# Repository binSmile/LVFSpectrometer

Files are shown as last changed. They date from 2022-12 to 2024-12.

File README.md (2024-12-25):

# LVFSpectrometer
[
](https://www.youtube.com/watch?v=VhedL_mU17M)

 Spectrometer based on linear variable filter with pulse-counter

The main idea was born, from need on spectral measurements of really weak light source (Scanning Tunneling Microscopy Light Emission).

My system consist of several parts:
- IDQuantique ID120 Single photo counter, Avalanced Photo Diode (APD) (with LV-TTL output)
- Optical system based on Thorlab's Cage system with several mirrors, beam splitter (90:10) and laser diode for illumination of collection point
- ESP8266 used as TTL pulse counter from APD (also used as DAC) 
- Linear Variable Filter (LVF) by Ocean Optics (now Ocean Insight) for 300-750 nm range.
- Arduino UNO used for movement step motor control
- Step driver TB6600
- 3D printed LVF holder.

Let's describe each part.
## DAC and pulse counter
In folder **Controllers**, you found ESPPulseCounter.ino - firmware for ESP8266. 
Previously it works on Arduino too, but it has some lags and minimal pulses integration time was 20 ms. ESP8266 - works better, the best time is 7 ms.
Before flashing firmware to ESP, you should set integration time, and minimum and maximum counting levels in Hz (counts per second), which correspond to 0V and 5V levels on DAC.

The main problem of counting pulses from is very short pulses from APD. Output pulse width is 25 **ns**. 
For counting, I use M74HC4040 (or SN74HC4040N) 12-Bit Asynchronous Binary Counters. And collect the number by MCP23017, 16-bit input/output port expander.  The ESP reads the number for one clock from port-extender. After that, the number was sent to serial and to MCP4725 12-bit DAC.
The DAC output was connected with Omicron Microscope to Aux2-port.
The layout of interconnection you can see in ESPPulseCounter-connection.svg

### Pulse_grabber.py
At the first time, I used simple python serial port grabber for collection information about intensity. At start of the script, it read a file with ESP firmware and store in file the values of DAC settings (such as min/max counts and integration time). These values may be used by some scripts for analyzing of Omicron Experimental Data.
This program writes counts to txt file and zip it in the end of work.

## Linear Variable Filter
I had a linear Variable Filter by Ocean Optics (You can read more here [Ocean Insight](https://www.oceaninsight.com/products/sampling-accessories/solid-sampling/linear-variable/lvf-hh/?qty=1)). 

## 3D-models
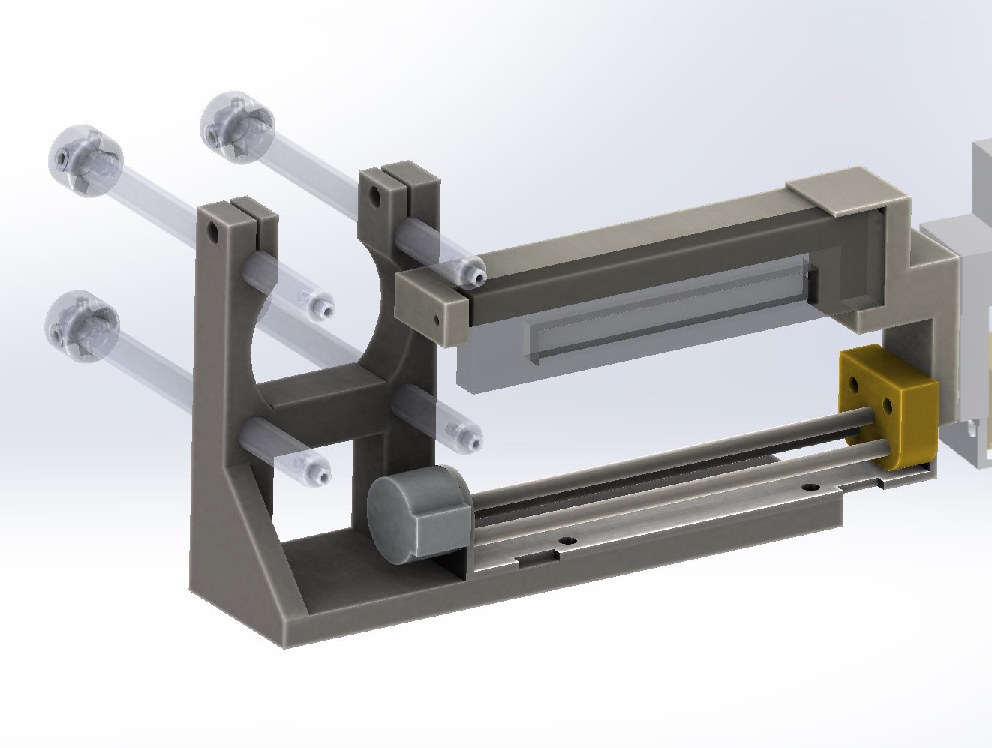
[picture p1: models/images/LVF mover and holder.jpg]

You can find models created in SolidWorks, I share to you the holder of LVF filter, and cage-holder for step-motor actuator.
If you plan to use it,  I recommend to you: paint model to black color,  and modify it for decreasing of shadows on light path. Also, in one of edge position, you will have touch of LVF-holder  with cage.

## Actuator
I bought  an assembled actuator with step motor from Aliexpress . It has DC 4-9 V  power supply. And it has driven by TB6600 step driver. I use 1/800 regime on driver, and it means, that driven shaft will have 12800 steps for 90 mm rod. 

## Arduino Move controller
You can find MoveControl.ino with Arduino Uno firmware and MoveControl-connection with connection layout. Also, I applied [GyverStepper2](https://alexgyver.ru/gyverstepper/). This is an excellent lib for stepper control.
For controlling of Arduino by serial, I used a simple communication  language presented is SerialCommunication-example sketch.

### Wires
- D4 to ENA+
- D3 to DIR+
- D2 to PUL+

### Commands for move controlling
Comand's structure is:
"Device","Comand","Value"
In this case the device number is **002**

- **002,brake,0** - stop
- **002,move,777** move on 777 steps forward
- **002,setspeed,-666** backward movement with speed 666 steps per piece of time
- **002,reset,0** set zero position 0

#### Service commands:
- **002,ready,0** return **m** - move, **r** - ready
- **002,Current,0** curent position
- **002,getStatus,0** 
- **002,setaccel,333** - you can set acceleration in step per sec^2. Set Zero is means movement with maximal speed, without smooth acceleration.

## SpecAcquisition.py
This is main programm for spectra Acusition.
Usually, I start it from console and use comand interface for experiment proceeding.
Todo: check stable work with long acqusition, more then 10 minutes.

### Main functions
- **GoHome()** - Function for manual approaching to home position. Setup doesn't have end move buttons.
- **DoPointSpectra(points=20,exposition=2,LVFLen=12000,name=SpecName)** - this command do 20 stops during 12000 steps lenght of movement, with 2 second acuqsition on each stop.

## SpecReader.py
Simple plotter of measured spectra.

## File tree
```
.
├── controllers                           - firmwares
│   ├── ESPPulseCounter-connection.svg    - wire connection DAC
│   ├── ESPPulseCounter.ino - ESP arduino - like firmware for pulse-counter DAC
│   ├── MoveControl-connection.svg        - wire connection of LVF mover
│   ├── MoveControl.ino                   - firmware for LVF mover
│   └── SerialCommunication-example.ino   - example of simple commmunication between PC and arduino.
├── models                                - directory with 3d-models for printing of LVF-holder.
│   ├── IDQ-LD.SLDASM
│   └── ...
├── README.md
├── Pulse_grabber.py                      - Loging of pulses from counter
├── SpecAcquisition.py                    - programm for Spectum acqusition with LFV
└── SpecReader.py                         - Simple plotter
```

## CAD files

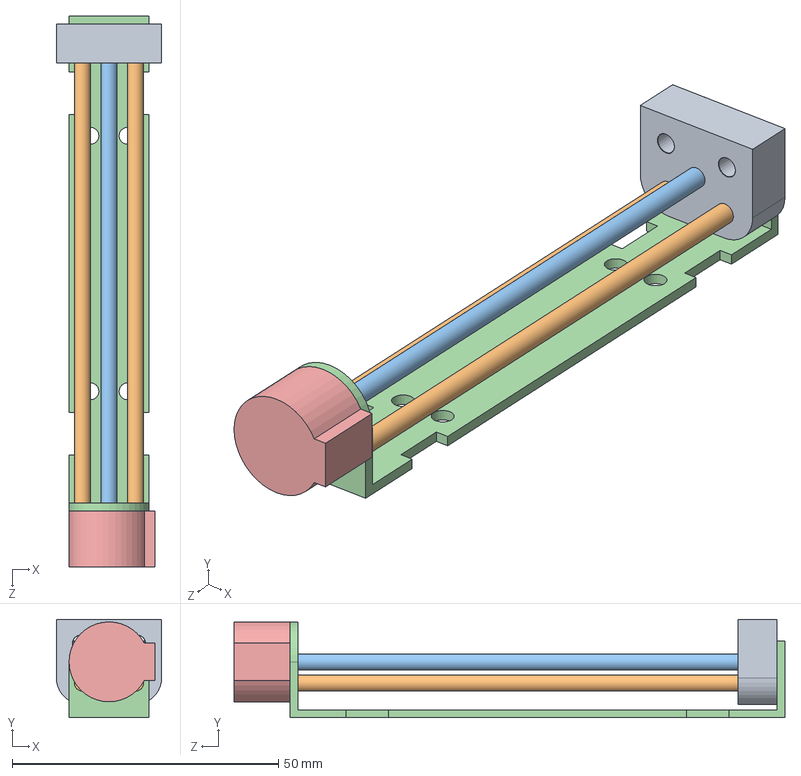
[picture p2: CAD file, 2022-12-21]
models/LinearMover.SLDASM
19.8 x 18.5 x 103.5 mm
Каретка^LinearMover
Направляющие^LinearMover
Ось^LinearMover
Станина^LinearMover
Мотор^LinearMover

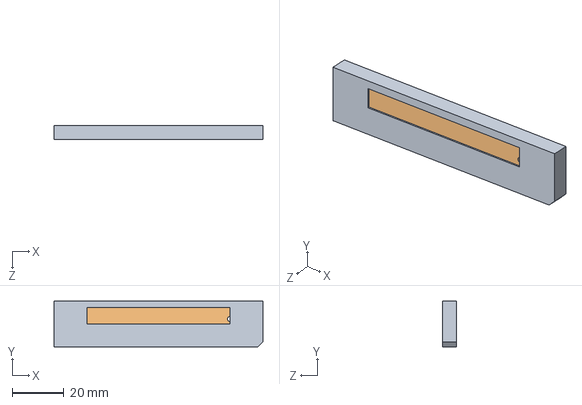
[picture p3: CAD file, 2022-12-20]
models/LVF.SLDASM
81.1 x 17.8 x 5.34 mm
LVF body
LVF glass

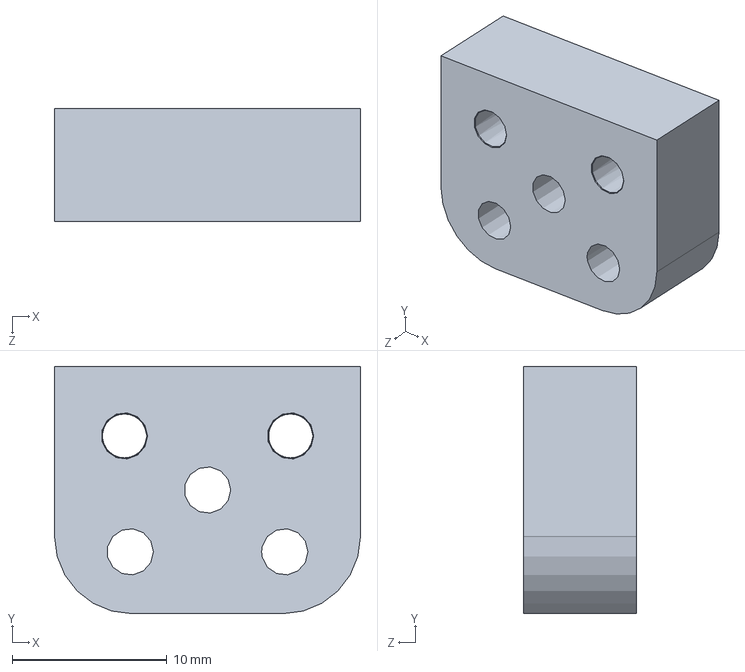
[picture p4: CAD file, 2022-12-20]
models/Каретка^LinearMover.SLDPRT
19.8 x 16.0 x 7.30 mm

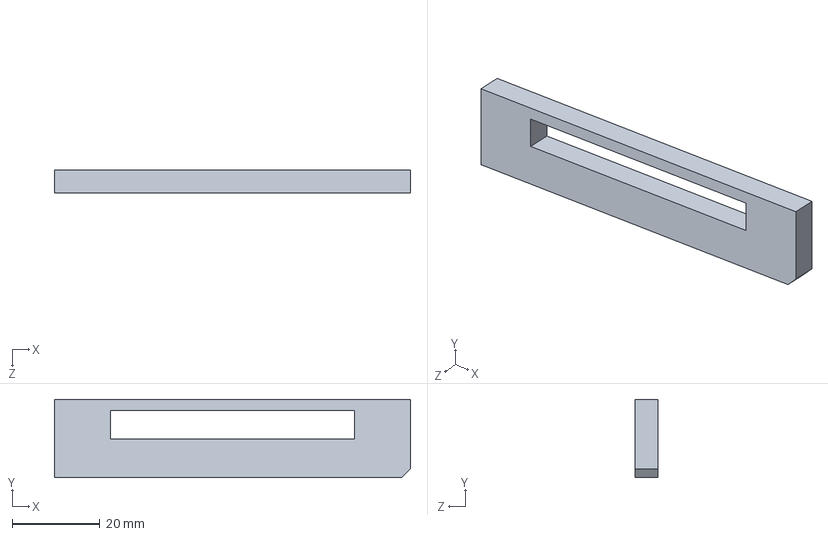
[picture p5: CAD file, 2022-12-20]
models/LVF body.SLDPRT
81.1 x 17.8 x 5.34 mm

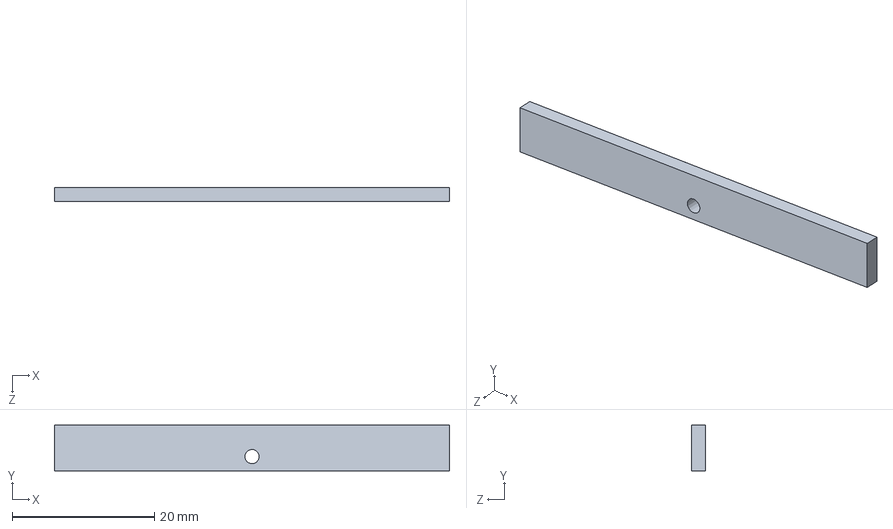
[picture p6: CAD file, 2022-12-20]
models/LVF glass.SLDPRT
55.5 x 6.41 x 2.00 mm

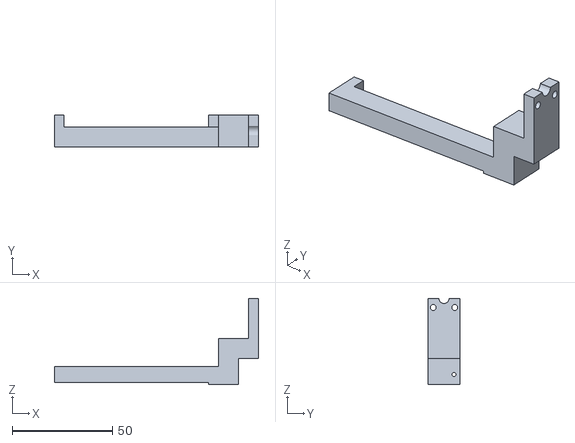
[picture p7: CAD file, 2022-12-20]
models/Скоба2^LVF holder_IDQ-LD.STL
102.0 x 16.0 x 43.0

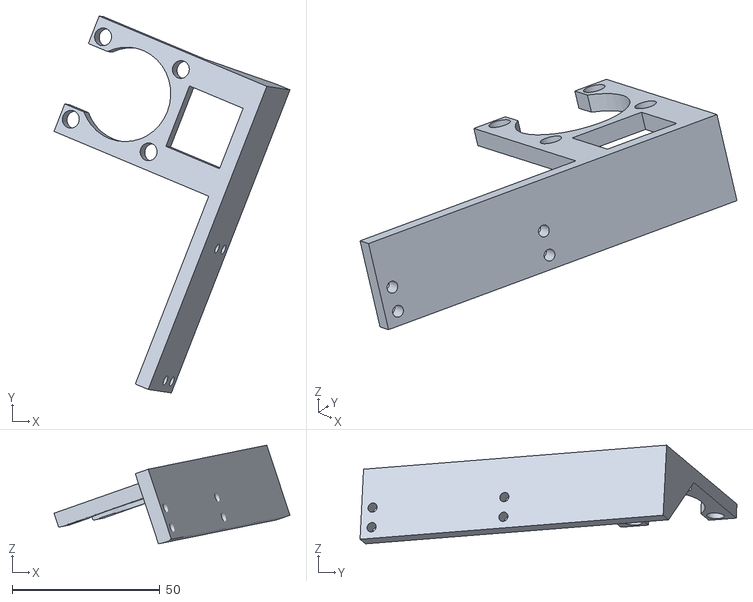
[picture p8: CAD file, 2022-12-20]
models/StepDriver holder^IDQ-LD.STL
79.8 x 127.5 x 33.4

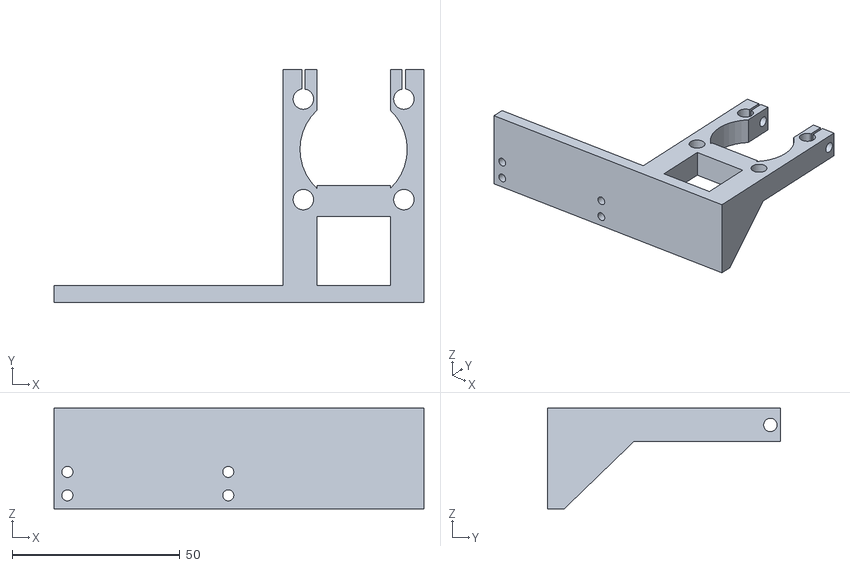
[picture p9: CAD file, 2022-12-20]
models/Деталь1^StepDriver holder_IDQ-LD.STL
110.4 x 69.5 x 30.0

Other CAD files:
models/OceanOptics-корпус.SLDPRT

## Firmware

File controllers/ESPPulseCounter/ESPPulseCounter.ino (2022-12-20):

int mestime = 10; // ms
long maxValue = 10800; // Hz
int noise = 800; // Hz

#include <Adafruit_MCP23X17.h>
#define BCMR D5
#define BCQ1 0
#define BCQ2 1
#define BCQ3 2
#define BCQ4 3
#define BCQ5 4
#define BCQ6 5
#define BCQ7 6
#define BCQ8 7
#define BCQ9 8
#define BCQ10 9
#define BCQ11 10
#define BCQ12 11

#define BCQ13 12
#define BCQ14 13
#define BCQ15 14
#define BCQ16 15
float outValue = 0;

Adafruit_MCP23X17 mcp;
#include <Wire.h>
#include <Adafruit_MCP4725.h>
Adafruit_MCP4725 dac;

// Set this value to 9, 8, 7, 6 or 5 to adjust the resolution
#define DAC_RESOLUTION    (12)

#include <string.h>
char unitID_in[10];
char command_in[10];
char data_in[100];

void setup() {
  Serial.begin(115200);
    Serial.flush();
  //while (!Serial);
  //  Serial.println("MCP23017  Button Test!");

  // uncomment appropriate mcp.begin
  if (!mcp.begin_I2C()) {
    Serial.println("Error.");
    while (1);
  }
  //  mcp.begin(0x20);

  // configure pin for port extender
  mcp.pinMode(BCQ1, INPUT);
  mcp.pinMode(BCQ2, INPUT);
  mcp.pinMode(BCQ3, INPUT);
  mcp.pinMode(BCQ4, INPUT);
  mcp.pinMode(BCQ5, INPUT);
  mcp.pinMode(BCQ6, INPUT);
  mcp.pinMode(BCQ7, INPUT);
  mcp.pinMode(BCQ8, INPUT);
  mcp.pinMode(BCQ9, INPUT);
  mcp.pinMode(BCQ10, INPUT);
  mcp.pinMode(BCQ11, INPUT);
  mcp.pinMode(BCQ12, INPUT);

  mcp.pinMode(BCQ13, INPUT);
  mcp.pinMode(BCQ14, INPUT);
  mcp.pinMode(BCQ15, INPUT);
  mcp.pinMode(BCQ16, INPUT);
  pinMode(BCMR, OUTPUT);
  dac.begin(0x60);
  digitalWrite(BCMR, LOW);
  digitalWrite(BCMR, HIGH);
  digitalWrite(BCMR, LOW);
  
}

void loop() {
  
static uint32_t tmr2;
if (millis() - tmr2 > mestime) {
  tmr2 = millis();

  //    uint8_t PA = mcp.readGPIO(0);
  uint16_t PAB = mcp.readGPIO();
  unsigned int value = PAB & 0b00001111111111111;
  //    unsigned int value = 0b00001111111111111;
  Serial.println(PAB, DEC);
  digitalWrite(BCMR, HIGH);
  digitalWrite(BCMR, LOW);


  //    int qState[] = {
  //      mcp.digitalRead(BCQ12), mcp.digitalRead(BCQ11), mcp.digitalRead(BCQ10), mcp.digitalRead(BCQ9), mcp.digitalRead(BCQ8), mcp.digitalRead(BCQ7), mcp.digitalRead(BCQ6), mcp.digitalRead(BCQ5), mcp.digitalRead(BCQ4), mcp.digitalRead(BCQ3), mcp.digitalRead(BCQ2), mcp.digitalRead(BCQ1)
  //    };
  //    unsigned int value = 0;
  //    for (byte i = 0; i < 12; i++)
  //    {
  //      value *= 2;
  //      value += qState[i] ;
  //    }
  //    value = value / 2;
  unsigned long freq = value * 1e3 / mestime;
  //Serial.println(value, DEC); // OUTPUT TRUE

  //Serial.println(freq, DEC);
  if (freq < noise) {
    freq = noise;
    outValue = 0;
  }
  else {
    outValue = (freq - noise);
    outValue = (outValue / maxValue) * (4095);
    outValue = int(outValue);
    if (outValue > 4095) {
      outValue = 4095;
    }
  }
  outValue = (freq - noise);
  outValue = (outValue / maxValue) * (4095);
  outValue = int(outValue);
  if (outValue > 4095) {
    outValue = 4095;
  }


  dac.setVoltage(outValue, false);
  //    outValue = 0;
  //    value = 0;

}

}

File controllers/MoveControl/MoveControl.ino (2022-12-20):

const uint8_t pin_ENA = 4;                // Вывод Arduino подключённый к входу драйвера ENA+.
const uint8_t pin_DIR = 3;                // Вывод Arduino подключённый к входу драйвера DIR+.
const uint8_t pin_PUL = 2;                // Вывод Arduino подключённый к входу драйвера PUL+.
// Вывод GND Arduino соединён с входами драйвера ENA-, DIR-, PUL-.
#include <GyverStepper2.h>
//https://alexgyver.ru/gyverstepper/
//GStepper<STEPPER2WIRE> stepper(1, pin_PUL, pin_DIR, pin_ENA);
GStepper2<STEPPER2WIRE> stepper(1, 2, 3, 4);

#include <string.h>
char unitID_in[10];
char command_in[10];
char data_in[100];


void setup() {                            //
  //  pinMode( pin_ENA, OUTPUT );          // Конфигурируем вывод Arduino как выход.
  //  pinMode( pin_DIR, OUTPUT );          // Конфигурируем вывод Arduino как выход.
  //  pinMode( pin_PUL, OUTPUT );          // Конфигурируем вывод Arduino как выход.
  Serial.begin(2000000);
  pinMode(13, OUTPUT); // Sets pin 13 as OUTPUT.
  Serial.flush();

  // установка макс. скорости в шагах/сек
  stepper.setMaxSpeed(400);
  // установка ускорения в шагах/сек/сек
  stepper.setAcceleration(500);

  // отключать мотор при достижении цели
  stepper.autoPower(true);
  // положительные смещения - от мотора
  stepper.reverse(false);


}                                         //
//



void loop() {
  stepper.tick();

    // график положения
    static uint32_t tmr2;
    if (millis() - tmr2 > 20) {
      tmr2 = millis();
      Serial.println(stepper.getCurrent());
    }



  int i = 0;
  char buffer[100];

  //если есть данные - читаем
  if (Serial.available()) {
    delay(100);

    //загоняем прочитанное в буфер
    while ( Serial.available() && i < 99) {
      buffer[i++] = Serial.read();
    }
    //закрываем массив
    buffer[i++] = '\0';
  }

  //если буфер наполнен
  if (i > 0) {

    //разбераем его на части отделенные запятой
    sscanf(buffer, "%[^','],%[^','],%s", &unitID_in, &command_in, &data_in);

  }

  //Исполнительная часть
  //Проверяем какому устройству пришли данные

  //тестовое устройство 001
  if ((String)unitID_in == "001") { //test serial read
    Serial.print("001,arduino recive: unit ");
    Serial.print(unitID_in);
    Serial.print("\n");
    Serial.print("command: ");
    Serial.print(command_in);
    Serial.print("\n");
    Serial.print("data: ");
    Serial.print(data_in);
    Serial.print("\n");
    unitID_in[0] = '\0';
    command_in[0] = '\0';
  }

  //пример выполнения команды устройством 002
  if ((String)unitID_in == "002") {
    if ((String)command_in == "brake") {
      stepper.brake();
    } else {
      if ((String)command_in == "move") {
        long  insteps = atol(data_in);
        stepper.setTarget(insteps, RELATIVE);
      }
      if ((String)command_in == "setspeed") {
        float news = atof(data_in);
        stepper.setSpeed(news);
      }
      if ((String)command_in == "setaccel") {
        float accel = atof(data_in);
        stepper.setAcceleration(accel);
      }
      if ((String)command_in == "reset") {
        stepper.reset();
      }
      if ((String)command_in == "ready") {
        if (stepper.tick()) {
          Serial.println("m");
        } else {
          Serial.println("r");
        }
      }
      if ((String)command_in == "getStatus") {
        Serial.println(stepper.getStatus());
      }
      if ((String)command_in == "Current") {
        Serial.println(stepper.getCurrent());
      }
    }


    // Serial.print("002,stepper recive: unit ");
    // Serial.print(unitID_in);
    // Serial.print(" command ");
    // Serial.print(command_in);
    // Serial.print("\n");
    unitID_in[0] = '\0';
    command_in[0] = '\0';
  }

  //пример выполнения команды устройством 013
  if ((String)unitID_in == "013") {

    if ((String)command_in == "on") {
      digitalWrite(13, HIGH);
    }
    if ((String)command_in == "off") {
      digitalWrite(13, LOW);
    }

    Serial.print("001,arduino recive: unit ");
    Serial.print(unitID_in);
    Serial.print(" command ");
    Serial.print(command_in);
    Serial.print("\n");
    unitID_in[0] = '\0';
    command_in[0] = '\0';
  }

}

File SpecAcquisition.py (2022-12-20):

import time
from datetime import datetime
import serial
import numpy as np
import pandas as pd
from _testcapi import Generic
from matplotlib import pyplot as plt


def test013():
    """
    Test script for blinking LED on Ardunino
    :return: None
    """
    ser.write(b'013,on')
    time.sleep(1)
    ser.write(b'013,off')
    time.sleep(1)
    ser.write(b'013,on')
    time.sleep(2)
    ser.write(b'013,off')


def Move(steps):
    """
    Just move
    :param steps: forward for positive, and backward for negative
    :return: None
    """
    print('Move to: ', steps)
    p0 = GetState()
    steps = int(steps)
    paim = p0 + steps
    ser.flushInput()
    ser.flushOutput()
    COMMAND = bytes('002,move,%s' % steps, 'utf8')
    ser.write(COMMAND)
    try:
        i = 0
        print('paim: ', paim)
        while GetState() != paim:
            # print('Get')
            i+=1
            # print(GetState())
            time.sleep(0.2)
            if i >= 1000:
                print('Long Operation! Brake!')
                StepperBrake()
                break

    except KeyboardInterrupt:
        print("KeyboardInterrupt has been catched!")
        StepperBrake()
    print('Stepper at ', GetState())


def GoHome():
    """
    Function for manual approaching to home position
    :return:
    """
    print('Write 0 if stepper at the home or -1 if stepper at the end.')
    steps = 1
    while steps != 0:
        steps = 0
        steps = int(input('How many steps I need to do: '))
        if steps == -1:
            Move(16 * PulsePerRev - 1)
        Move(-steps)

    COMMAND = bytes('002,reset', 'utf8')
    ser.write(COMMAND)
    print('Okey. We at home.')



def DoPointSpectra(points, exposition, LVFLen, name='Test'):
    """
    Main function for getting spectrum
    :param points:     stops counts on the move range
    :param exposition: time in seconds signal collection
    :param LVFLen:     range of move along LVF
    :param name:       name for save file
    :return: DataFrame with spectra in each point
    """
    # GoHome()
    HomePosition = GetState()
    start = datetime.now()

    i = 1
    spacer = LVFLen / points
    print('Get point 1')
    Acquisition(1)
    Spectra = [[GetState()] + Acquisition(exposition)]
    for l in range(points):
        i += 1
        print('Get point %s' % i)
        Move(spacer)
        data = [GetState()] + Acquisition(exposition)
        Spectra += [data]
    print('GoHome')
    Move(-GetState()+HomePosition)

    Spectra = pd.DataFrame(Spectra,
                           columns=['Pos', 'Int', 'Num', 'Std', 'Mean'])
    # Spectra.set_index('Pos', inplace=True)

    x = [3280, 7360]
    y = [733 + 12.1, 468 + 12.1]
    a, b = np.polyfit(x, y, 1)
    Spectra['W'] = Spectra['Pos'] * a + b
    Spectra = Spectra.set_index('W')

    startLogging = start.replace(microsecond=0).strftime('%Y-%m-%d_%H-%M-%S')
    name = startLogging + '_'+ name
    Spectra.to_excel(specdir + name + '.xlsx')

    plt.errorbar(Spectra.index, 'Int', yerr='Std', data=Spectra)
    mins = max(Spectra['Int'].min(),0)
    maxs = max(Spectra['Int'].max(),1)
    plt.vlines(745, mins, maxs,colors='k')
    plt.vlines(480, mins, maxs,colors='k')
    plt.hlines(Spectra['Int'].mean(), 880, 745,colors='k')
    plt.title(name)
    plt.suptitle("Exposition: %s" % exposition)
    plt.savefig(specdir + name + '.png')
    with open(specdir+name+'_info.txt','w') as info:
        info.write('Exposition,%s' % exposition)

    print('Gotcha!')
    print(name)
    return Spectra


def SetSpeed(speed):
    COMMAND = bytes('002,setspeed,%s' % speed, 'utf8')
    ser.write(COMMAND)


def StepperBrake():
    COMMAND = bytes('002,brake', 'utf8')
    ser.write(COMMAND)


def SetAccel(Accel):
    COMMAND = bytes('002,setaccel,%s' % Accel, 'utf8')
    ser.write(COMMAND)


def GoToEnd():
    Move(16 * PulsePerRev - 1)


def GetState():
    ser.readline()
    ser.flushInput()
    ser.flushOutput()
    # COMMAND = bytes('002,Current', 'utf8')
    # ser.write(COMMAND)
    try:
        time.sleep(0.2)
        buff = ser.readline()
        reading = int(buff.decode('utf8')[:-2])
    except:
        ser.flushInput()
        ser.flushOutput()
        time.sleep(1)
        buff = ser.readline()
        print('pause at get state')
        reading = int(buff.decode('utf8')[:-2])
    # print('State: ',reading)
    return reading


def Acquisition(atime):
    """
    Acuisituion of intensity from pulse counter.
    :param atime: time in sec
    :return: [np.median(Acq), len(Acq), Acq.std(), np.mean(Acq)]
    """

    i = 0
    t_end = time.time() + atime

    Acq = np.array([])
    while time.time() < t_end:
        sercount.flushInput()
        sercount.flushOutput()
        data = sercount.readline()[:-2].decode('utf-8')

        try:
            Acq = np.append(Acq, int(data))
        except:
            print('Miss Value')
    # return [median, Num, Std]
    print(np.median(Acq), np.mean(Acq), len(Acq), Acq.std())
    return [np.median(Acq), len(Acq), Acq.std(),np.mean(Acq)]


def FalseGet():
    """It need sometime, when you don't use serial port during the long time, you must flush it, before normal working"""
    sercount.flushInput()
    sercount.flushOutput()
    sercount.readline()[:-2].decode('utf-8')


if __name__ == '__main__':
    bbdir = 'C:\\..\\GlobalProjects\\STM-Electroluminescence\\ExpData\\Omicron results\\'
    bdir = bbdir + 'PulseGrabber\\'
    specdir = bbdir + 'Specs\\'

    LVFport = 'COM8'        # Port to move controller
    PulsePerRev = 800       # Step Driver regime
    PCounterPort = 'COM7'   # Port to Pulse counter

    # LVFLen = 16 * PulsePerRev * 0.95
    LVFLen = 500            # Length of holder shadow in steps
    FullLen = 7360          # Length of usefull part of LVF


    # Connect to pulse mover
    ser = serial.Serial(LVFport, 2000000, timeout=1)
    print('Step Driver set at %s pulse/rev' % PulsePerRev )
    # Connect to pulse counter
    sercount = serial.Serial(PCounterPort, 115200, timeout=1)

    # test013()
    # GoHome()


    Move(10000)

    # spec = DoPointSpectra(points=50,exposition=1,LVFLen=LVFLen)
    # DoPointSpectra(points=5,exposition=1,LVFLen=100)
    # GoToEnd()
    if True == True:
        # Spectra = DoPointSpectra(points=5,exposition=60,LVFLen=7000,name='Test')
        print('Position on AVR: %d' % GetState())
        GoHome()
        SpecName = 'STM-LE_Au-Au_10nA_-2.5V' #input('Spec name:')
        Spectra = DoPointSpectra(points=20,exposition=2,LVFLen=12000,name=SpecName)
        # plt.errorbar(Spectra.index, 'Int', yerr='Std', data=Spectra)


    # ser.close()
